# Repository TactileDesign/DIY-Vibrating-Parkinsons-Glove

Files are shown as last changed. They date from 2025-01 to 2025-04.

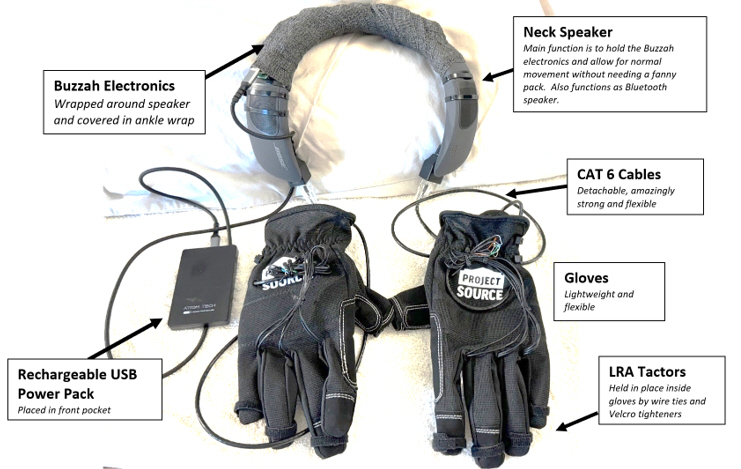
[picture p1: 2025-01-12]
1 - Buzzah Neck Build.jpg

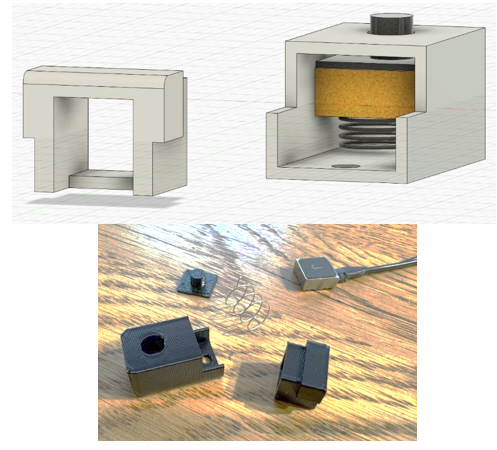
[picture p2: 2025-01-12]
1 - tactor.jpg

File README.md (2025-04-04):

# DIY Vibrotactile Parkinsons Glove (Neckbuild Buzzah Design)

This design makes use of Kris Wilk's Buzzah electronics design to drive LRA based tactors.  There are two things new in this build that add to Kris's design: 

1.  The gloves feature a new spring-based LRA tactor design that provides more energetic and focused vibrations than comparable foam-based LRA tactors.   When foam is used to decouple LRA tactors, significant energy is lost due to internal friction in the foam.  No energy is lost when using springs for this function since springs are almost perfectly elastic.  See the separate pdf for a detailed discussion of these new spring tactors.

2.  The electronics are housed on a bluetooth neck speaker.  This keeps the wires out of the way compared to fanny pack versions.  The bluetooth speaker can also sync with your smartphone as a speakerphone and mp3 player.

Note:  There are two files here.  The 'building description" file details how to build the gloves and tactor.  The "design considerations" file discusses theoretical issues regarding LRA-type tactors.

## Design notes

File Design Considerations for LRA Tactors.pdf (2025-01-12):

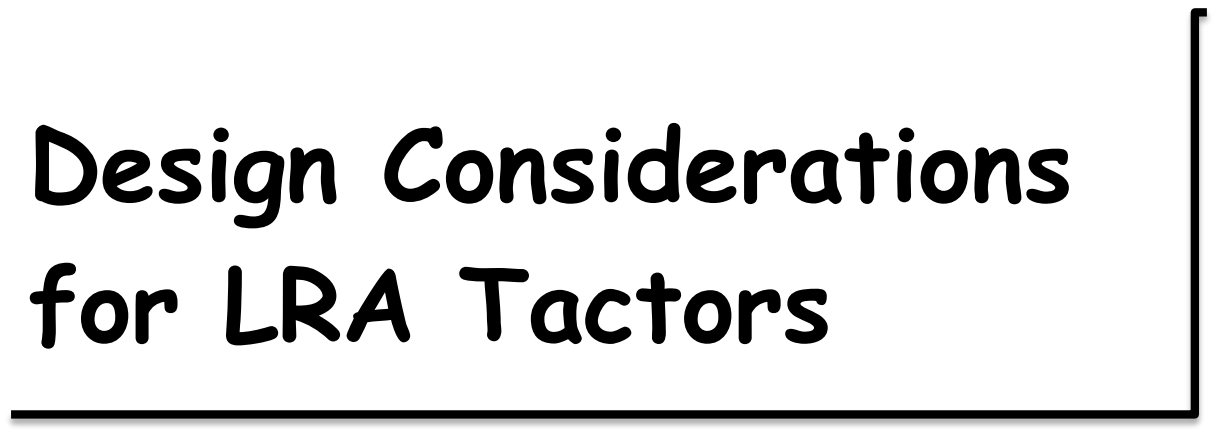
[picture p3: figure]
Design Considerations for LRA Tactors

### Introduction

What follows is a description of the theoretical design criteria that were considered in designing a tactor housing for a square shaped z-direction LRA. Detailed instructions and 3D print files for constructing tactors and fitting them to a glove are provided with the Buzzah neck build instructions. While I developed this tactor housing to use in my Buzzah Neck Build, but it would work in any LRA-based design.

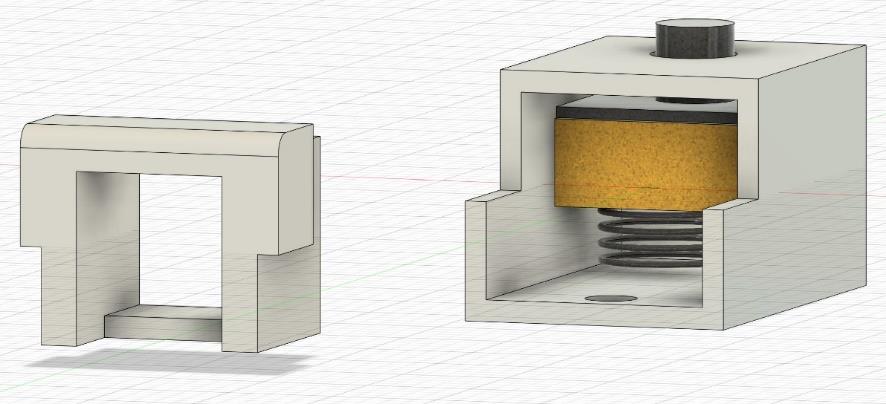
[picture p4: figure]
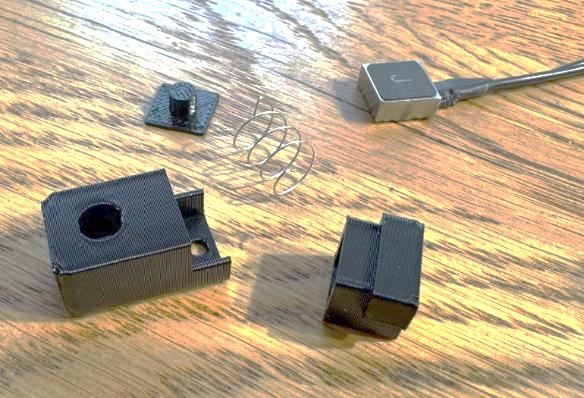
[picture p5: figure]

# Physical Principles of LRA Tactors

Imagine a paint can that is vibrates inside a shaker case as shown here. When the case pushes up on the can, Newton’s 3rd law tells us that the case must experience a downward reaction force
from the paint can. This downward force on the case does not create any motion of the
case because the case is “grounded” on a table which does not allow motion in the
downward direction. However, when the case alternatively pushes downward on the paint can, the inertia of the can results in an upward force on the case. If this upward force from the can is greater than the weight of the case, the case will be lifted off the table. The scenario just described is exactly analogous to what is going on in an LRA vibrator that is being driven by a Buzzah driver. Instead of having a paint can, the LRA
has a relatively massive magnet that is vibrates up and down inside its case, resulting in
the vibrations of the case we observe externally.

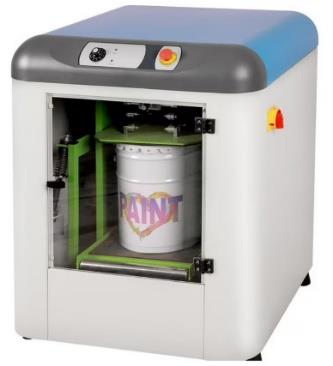
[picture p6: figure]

To illustrate the challenges of tactor design for an LRA, consider the following demonstration. In (A), a vibrating LRA vibrates vigorously off a table like the paint shaker our previous example. In (B), a finger pushes gently downward on the vibrating LRA. If you were to perform this experiment yourself, you would find that the LRAs vibration is quickly grounded out by the table, even with only a very slight pressure from your finger. However, if a weak spring is placed between the vibrating LRA and the tabletop as in (C), you would find that the LRA continues to vibrate vigorously up and down as long as you don’t push so hard as to completely compress the spring against the tabletop. As we design our tactor, we must likewise incorporate an elastic element within our tactor housing that allows a free up and down LRA vibration as in (C).

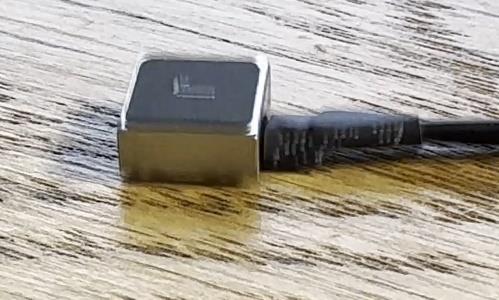
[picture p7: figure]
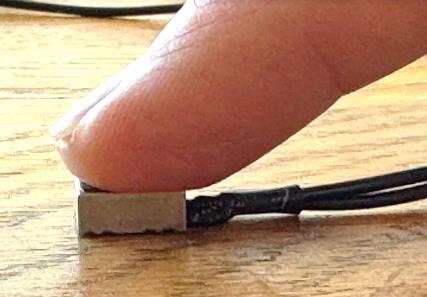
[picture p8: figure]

(A) | (B) | (C)

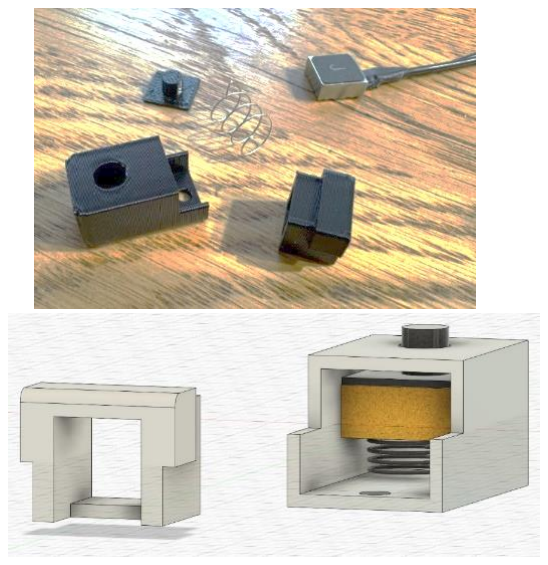
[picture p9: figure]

The 5 elements of the LRA tactor I designed are illustrated here. The LRA buzzer is sandwiched between a button plunger from above, and a weak spring from below. When the button is depressed, the internal plunger is pushed away from the top of the tactor housing. This keeps the LRA from mechanically grounding out to the top of the case which is itself grounded by the glove finger elastically holding the case against the fingertip. The LRA vibrates freely within its rectangular enclosure that is closed in by the endcap which is held in place by a tight friction fit. No fasteners are required. The endcap fits tight enough not to loosen from normal use, but not so tight that it cannot be removed with needle nose pliers. The window in the endcap is big enough to allow the electrical leads to exit, but small enough to keep the LRA and spring from vibrating out of their box inside the case. The hole in the bottom of the case allows the tactor to be attached inside a glove using a small plastic wire tie.

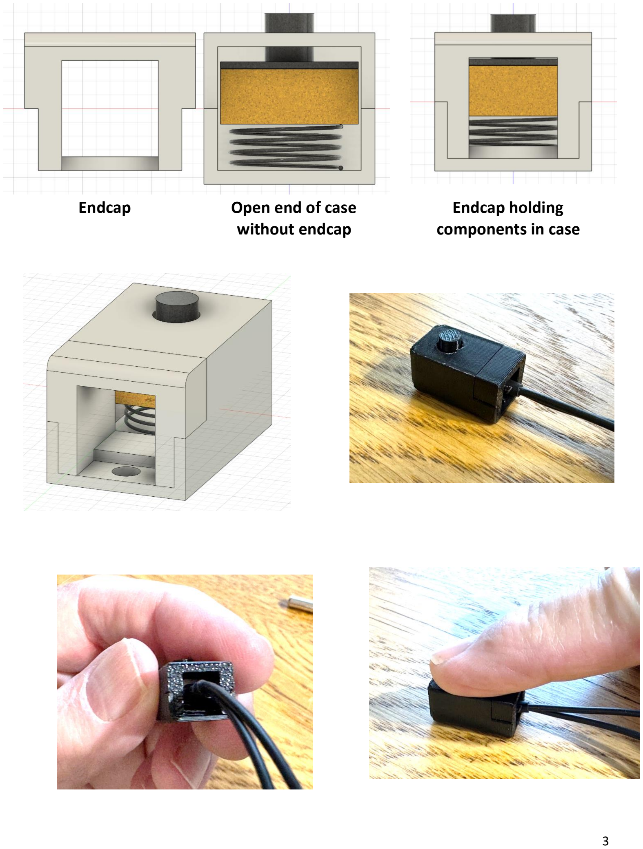
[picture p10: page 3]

Endcap | Open end of case | Endcap holding
| without endcap | components in case

# Determining Spring Characteristics

Before deciding to employ a spring to decouple the LRA from the tactor enclosure, I tried various types of springy foam and sponges collected from around the house and from various hardware store products. But all samples damped the vibration of the LRA to unacceptable levels. One can easily observe the damping effect that is introduced by foam by performing this simple test: In figure (A), a buzzer is hooked to an LRA driver and decoupled from the tabletop using a weak spring of length 11 mm. The buzz that is experienced with the spring is then compared to the same buzzer decoupled from the tabletop by foam with 11 mm thickness as we see in figure (B).

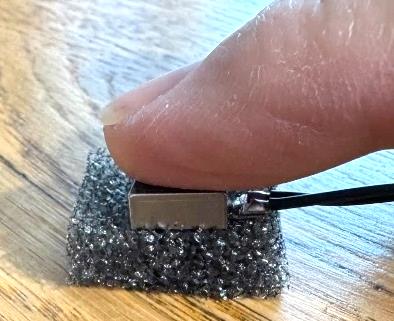
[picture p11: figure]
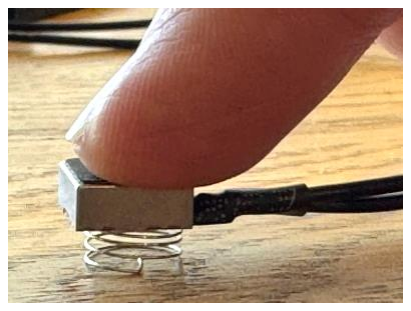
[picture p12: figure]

(A) (B)

When I performed this test, I found that the foam significantly damped the motion of the LRA buzzer compared to the spring. With the spring, the perceived buzz amplitude felt uniform, with no change in amplitude as I increased loading force as per Tass specifications to achieve the required 0.5 mm preload skin indentation. However, the foam gave a highly non-linear response, with perhaps 20% damping compared to the spring for very light preloading, and well over 50% damping for stronger preloading. There are two properties of the foam that caused this. First, all the foam I could find was too stiff, creating too strong coupling with the table, thereby grounding out vibrations. The stiffness of the foam appeared to increase non-linearly with increased deflection, leading to an observed rapid increase in damping at higher preloading. One might think we could solve the grounding problem if we could just find weaker foam. However, foam has another problem: It is inherently inelastic. Imagine trying to bounce a ball on foam and you realize the ball barely bounces because of the foam is eating up energy internally through damping. So, even if we could find a foam that feels sufficiently cushy, it would still be problematic due to its inherent damping characteristics.

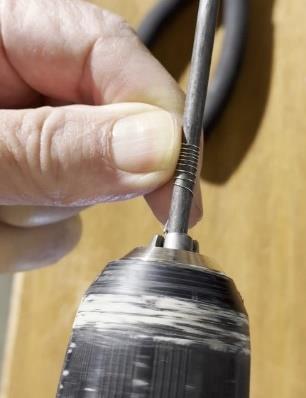
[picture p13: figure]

Finding a sufficiently weak spring with the proper dimensions as shown in figure (A) was a
challenge. There are plenty of springs on Amazon that are the right size, but they were all
way too strong for this application, creating too strong coupling between the tactor housing and LRA. Suppliers online such as https://www.thespringstore.com/ advertise 70 trillion springs available. However, 99.9999% of their springs are only available by special order, outrageously priced at $4-$10 per spring. Still in my design phase, I was still not sure about the ideal spring force constant, wire diameter, coil diameter, number of turns, and coil pitch, so special ordering high priced springs for testing was not a viable option. Then my wife suggested I make my own springs. It turns out they are very easy to make as illustrated here on YouTube: https://www.youtube.com/shorts/M9Lnm1P6_70 . After experimenting with the many parameters by trial and error, I finally settled on the criteria discussed below.

### Wire type

Once I had the idea to make my own springs, I quickly found that guitar strings were ideal for this purpose because they are cheap and come in many gauges. Looped end guitar string of diameter 0.012 inch proved to be idea. Each string makes up to 7 springs, but I would suggest buying 10 strings so you have plenty to for practice – total cost $11.90 on Amazon.

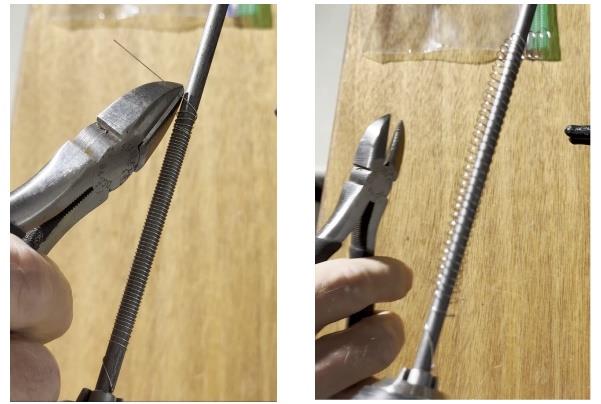
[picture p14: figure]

### Rod Diameter

The coil expands quite a bit after unwinding from the rod. And different gauge wire expands to make different diameter coils. Through trial and error, I found that 0.012-gauge wire yields a perfect spring diameter of 8.5 mm when wound and released from a 3/16” steel rod. An 8.5 mm diameter coil fits nicely under the 10 mm square LRA, and it is big enough that it does not vibrate out the wire window in the tactor. The rod can be purchased from Home Depot for $3.92 (see tools list). Note that the rod comes coated with very dirty oil and you will need to wash it and cut it down to about 18 inches before you start making springs.

### Number of Coils

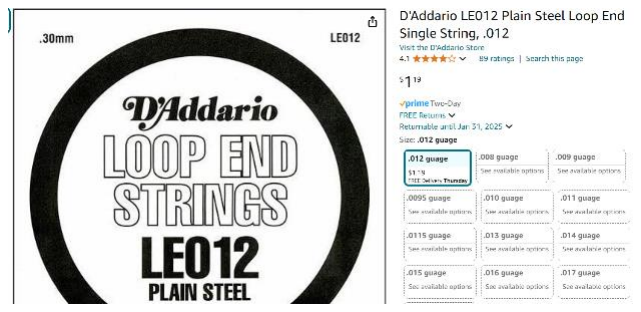
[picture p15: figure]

There are two factors to consider in determining the optimal number of coils to use in springs. We don’t want to have too many coils because, when the button is fully depressed, the compressed coils start taking up too much space in the bottom of the enclosure and can bottom out. Alternatively, having too few coils leads to too large of an angle between the spring and the LRA bottom which can cause binding in the chamber. After much experimenting, I ended up settling on the optimal number of coils to be 4.5. Having the half-coil on the end helps keep the spring from canting during use. As you see in the pictures shown below, I also put a small bend on either end of the spring to keep the ends from snagging and slipping up the side of the LRA.

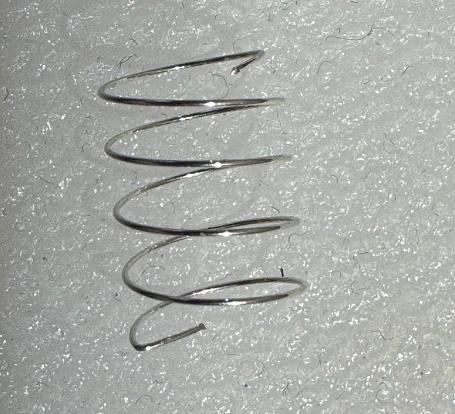
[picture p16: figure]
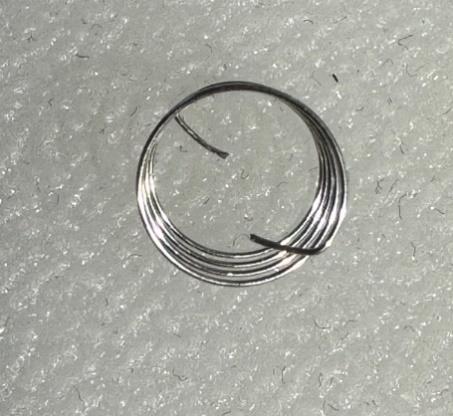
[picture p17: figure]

### Skin Preloading Displacement and Spring Rest Length

The crucial parameter of skin preloading displacement is perhaps the most important adjustable parameter of the tactor since it relates most directly to the quality of the vibration sensation that the tactor imparts to the fingertip. I accordingly spent a lot of time making sure I matched Dr. Tass’s specifications for this parameter as closely as possible.

In the diagram shown at right, we see the ideal 250 Hz tactor vibration signal that is to be applied to a fingertip in the Tass specifications from his device specs paper: https://pmc.ncbi.nlm.nih.gov/articles/PMC5624565/ . The vibration signal consists of a small 0.03 mm amplitude vibration from the buzzer on top of a 0.5 mm preloading displacement. The preloading
displacement is the distance the button contact protrudes into the skin when
the tactor is mounted to a fingertip before the buzzer vibration is applied.

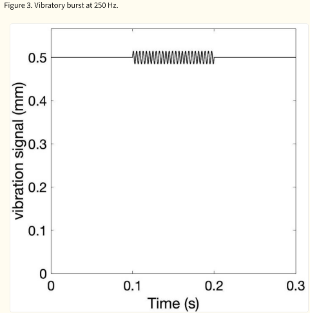
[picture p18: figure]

Consider the diagrams shown below to understand how preload skin displacement is achieved by our tactor/finger system through a balance between spring stiffness and skin elasticity. In (fig A), we see the spring at my ideal initial rest length, RL = 11 mm, which is coincidentally the same height as the case, C. In (fig B), the 11 mm spring is compressed to fit within case 4.5 mm cavity height, I, that exists under the rectangular LRA before the button is depressed. In (fig C), the button is depressed by an unseen finger, further compressing the spring below to a length, F. The fraction of the button extending over the top of the enclosure, and thus protruding into the fingertip skin, is the ideal preload skin displacement, PL = 0.5 mm. Figure C then illustrates what the button should look like under the finger when a tactor is mounted to the finger.

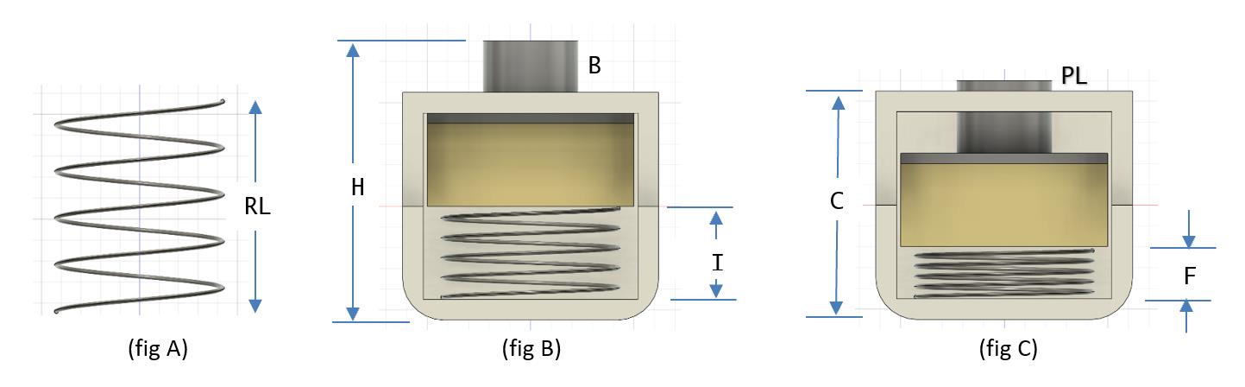
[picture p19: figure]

We see above that, since the button moves downward as the finger is positioned on the case, the preload skin displacement is not simply equal to the initial button height, B, above the case before the tactor is mounted to a fingertip. Instead, the preload skin displacement depends on the preloading force the spring exerts on the skin when the button is pushed. Since fingertip stiffness of the skin is much greater than that of the weak spring, most of the button travel is taken up by the spring, with only a fraction going into skin indentation.

The variable in our tactor that controls the magnitude of preload skin displacement for our tactor is the spring stiffness. As spring stiffness is increased, the preload skin displacement for a mounted tactor is correspondingly increased. The stiffness of a spring can be adjusted by small increments by changing its initial rest length. Stretching out a spring to have a longer initial rest length will make it stiffer. Winding a new spring with closer coils will result in a spring that is less stiff. If larger changes to stiffness are required, a new spring can be made with larger or smaller diameter guitar wire. Larger diameter wire leads to stiffer springs. We nominally use 0.012” diameter wire, but guitar wire comes in all diameter increments from 0.009” to 0.022”. However, only the gauges from 0.011” to 0.013” are likely to produce springs in a useful stiffness range for our tactor. As discussed previously, if you want to experiment with different gauge wire, you may need to use a different rod diameter to end up with a useable spring diameter.

Since spring tension can only be modified with the spring
outside the tactor housing, a process of trial-and-error testing
must be undertaken to determine the ideal spring rest length and wire diameter for a particular user.

There are three methods I devised to measure the preload skin displacement resulting from a particular spring in a mounted tactor. In method 1, I simply adjusted spring stiffness by trial and error to achieve a subjective perception of a relatively light preloading force that produced a robust and localized “zing” sensation on my fingertips when the spring was in a tactor
housing. Small changes in initial spring length result in
significant changes in spring stiffness. If a spring is stretched to

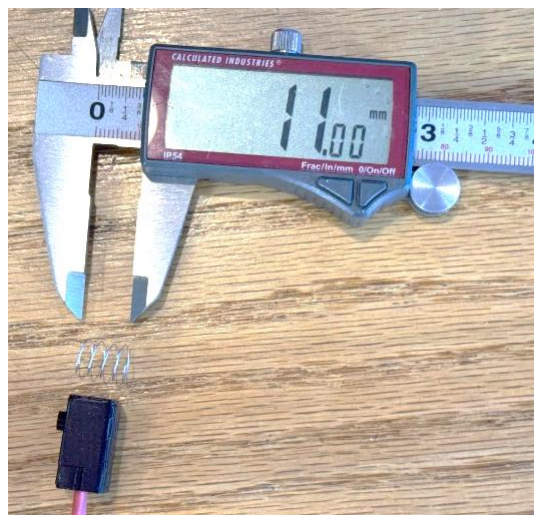
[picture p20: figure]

a longer initial length, the the preload displacement becomes greater, and the vibratory sensation increases. However, if a spring is too stiff, the vibrations cause finger bones to also vibrate which compromises therapeutic efficacy as Dr. Tass explains. If your spring is too strong, you need to make a new spring with closer coils and thereby less initial length. However, if a spring is too weak, therapeutic efficacy may also be compromised if the “zing” becomes too mild to clearly sense. I therefore sought to maximize the zing without getting vibrations transferring into my bones. Using the above trial-and-error method, I arrived at my ideal spring parameters of RL = 11 mm, number of coils = 4.5, and wire diameter = 0.012 inches.

While I was satisfied with the buzz sensation I achieved with these settings, I worried that my subjective method might not be yielding the proper Tass preload displacement of 0.50 mm. I therefore devised method 2, illustrated below, as an objective way to directly measure preload displacement and validate my subjective technique in method 1. In method 2, a special test tactor is 3D printed which has a 4 mm hole in its bottom surface. This hole in the bottom allows a feeler gauge to probe to the bottom of an LRA framed inside the assembled tactor. Note that two people are needed to perform this measurement.

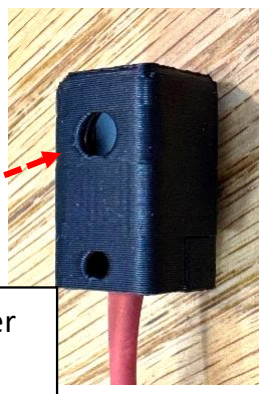
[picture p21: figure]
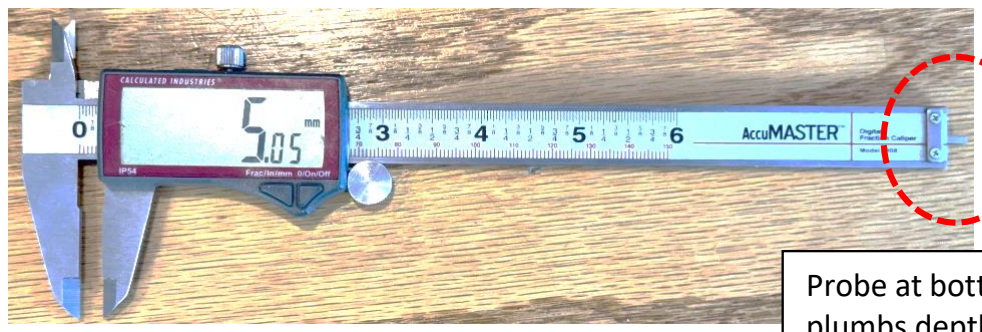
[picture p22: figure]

Probe at bottom of caliper plumbs depth of LRA
through hole in bottom

The difference in probe depth, before and after the tactor is mounted to a fingertip, yields the change in chamber height, I – F. The change in chamber height is likewise equal to the change in button height that occurs when the finger is mounted on the tactor.

Cℎange in Cℎamber Heigℎt = Cℎange in Button Heigℎt

I − F = B − PL

The tactor preload displacement, PL, is then found by,

PL = B − (I − F)

The initial button height, B, can be precisely found by subtracting the case height, C, from the initial overall tactor height, H,

Initial Button Heigℎt = Overall Tactor Heigℎt − Case Heigℎt

B = H − C

Plugging in the actual measurements I made on my test tactor using an 11 cm spring with 4.5 coils, I obtained,

PL = | H | − | C | − | (I | − | F)

= 13.4 mm − 10.94 mm − (5.01 mm − 3.03 mm) = 0.48 mm

Happily, method 2 verified that the ideal 11 mm spring rest length that I subjectively obtained from method 1, yielded a measured preload 0.48 mm skin displacement that was quite close to the ideal 0.50 mm value that is specified my Dr. Tass.

The above measurements were made under ideal conditions while sitting motionless at a desk. Under less ideal conditions, users may be picking things up or pushing on some external surface. When the tactor is squeezed between a fingertip and some external object, the finger will exert a stronger force against the spring and cause preload displacement to be reduced. When this happens, the perceived vibrational amplitude is increased by about 20%. I don’t view this necessarily as bad since Dr. Tass has suggested some modulation of amplitude might actually be helpful in therapy. Note also that the above measurements were taken on an early tactor prototype. After further testing I reduced the button shaft height by 0.3 mm to allow for a bit more room for the compressed spring to keep it from bottoming out when the button is depressed.

Note that my case measurements, H and C, used above do not exactly match the corresponding parameter settings I had programmed into my 3D printer. For example, I had my case height set at 11 mm in my printer, but it actually came out to be 10.94 mm when measured. Therefore, H and C had to be measured on a real tactor because of the slight deviations that occur in the process of printing.

While method 1 and method 2 both provide reliable ways to adjust spring stiffness for individual users, I worried that these methods may not be easy to replicate by novice tactor builders. I then devised a third method based on subjective protrusion feel that is much easier to implement for a novice. In method 3, a set of solid reference tactors are 3D printed with fixed PL button heights of 0.3 mm, 0.4 mm, 0.5 mm, 0.6 mm and 0.7 mm. The test tactors are used as tactile references for users to compare to the feel of a preload displacement being caused by a spring in a tactor that is being tested. The objective in method 3 is to determine an initial spring length that yields a strong localized “zing” when the button is depressed to a height equivalent to the 0.5 mm reference tactor. The additional references are provided to demonstrate to the user what “too high” or “too low” feels like.

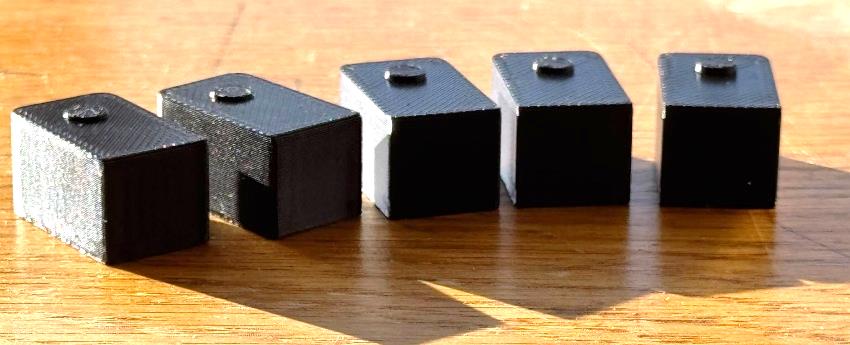
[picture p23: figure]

Dummy tactors used to demonstrate the feeling of the ideal preload displacement

### Tactor/Finger Mounting

When the tactor is mounted to a fingertip, its entire top surface should be making contact with skin to help block skin vibrations from the button from moving beyond the button area as per Tass specifications. The process of determining the proper tightness by which the tactors are lashed to the fingertip must be performed in concert with the above process to determining spring stiffness. If a tactor is lashed too tight, it will depress the button too far when using a particular spring and result in vibrations that vibrate into finger bones. If you lash the tactor too loosely, the button will be less depressed and result in weaker vibrations. The tactor needs to be tight enough not to slip off the finger during normal use, but not so tight as to cause discomfort. The reference tactors from method 3 above can also be used to help gauge the tightness that achieves proper PL height. Velcro fingertip tighteners are the most reliable way to achieve a precise and reliable lashing that does not stretch out over time. However, I find the Velcro tighteners too annoying because of the loss of dexterity and the fact they tend to grab to fabrics I touch. I alternatively spent much time and energy to find a glove that has the proper finger diameter and elasticity to hold the tactors to my fingers with the correct preloading force. In my quest to find the perfect glove that could be used without Velcro, I tested nearly 20 pairs of gloves from Lowes and Home Depot. I describe my glove choice later in the building section of this grand treatise.

### Initial Button Height

The current tactor I use is designed to have a nominal button height, B = 2.2 mm. The chamber that houses the spring and LRA ostensively allows for I = 4.5 mm of button travel since the LRA thickness is 4.0 mm, the case thickness is 1.0 mm, and the flange thickness is 0.5 mm. Using a button shaft height of 3.2 mm yields F = 2.8 mm in the bottom of the chamber to accommodate the compressed spring windings. The 2.8 mm also allows sufficient space to accommodate the 0.03 mm vibration amplitude along with occasional over-compression which occurs when
picking up heavy objects, and
possible variances occurring in the 3D printing process.

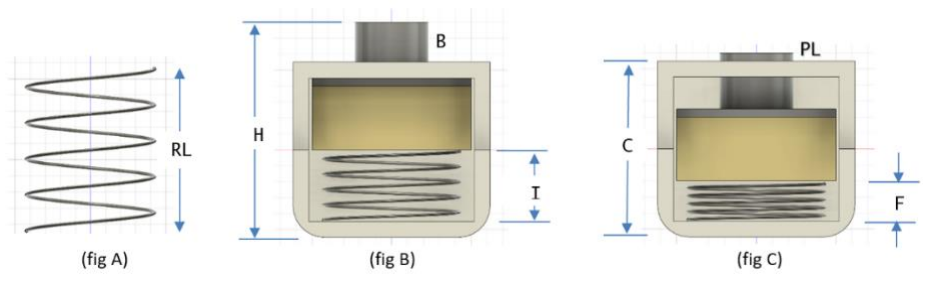
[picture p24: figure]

One might think that the nominal 9 mm chamber height could be reduced if B was reduced in order to make a smaller tactor. However, there is a practical concern that requires B to be at least 1 mm. Before the button is depressed, the button flange is forced up against the inside chamber ceiling by the spring. This flange must be pushed clear of inner ceiling of the finger mount in order to facilitate the free vibration of the LRA. Since the vibrational amplitude is only 0.03 mm, the clearance of the button flange from the inner chamber ceiling might not seem to be an issue. However, the top of the spring is angled slightly due to coil pitch, so there is a tendency for the button flange to be slightly canted by the top of the spring. In practice, I found that the flange needs to be pushed in at about 1 mm to safely clear the inside enclosure ceiling and allow free LRA vibration. So, theoretically, B could have been reduced in the tactor design (requiring a slightly stiffer spring). With B = 1.0 mm, the user would only need to depress the button by 0.5 mm to achieve the proper PL. However, when I tested tactor designs with shorter B heights, I found it was too easy for the button to slide off my fingertip when I was performing activities with my hands. With B = 2.2 mm, the buttons reliably remain in contact with my fingers, actively providing therapy, when performing activities that jostle the tactors.

### Vibrational Amplitude

The vibrational amplitude of the LRAs in this tactor design is set in the Buzzah software. In all the measurements described previously, I had my amplitude set at 100%. Unfortunately, I could not think of any simple way to actual measure the vibrational amplitude to verify that it matched the 0.03 mm amplitude in the Tass specifications. So, this is a parameter that we must adjust based on user perception. My philosophy when adjusting amplitude is to deliver the highest vibrational amplitude that does not feel like it vibrates into my finger bones. The 100% Buzzah setting yields a stronger perceived fingertip vibration when using the tactor compared to how I used to apply my treatment with an LRA held directly to my fingertip without a tactor. Even though the buzz is stronger when using this tactor, I have left the amplitude at 100% since it does not feel like it is going into my bones when spring tension and mount tightness are adjusted as described above. If I ever felt like I was getting too much vibrational amplitude, I could adjust it lower in the software settings. However, I could not obtain a larger amplitude since I am already at the high limit of my dynamic range without increasing PL.

In summary, skin preload displacement and amplitude are adjusted by trial and error to achieve sufficient zing to clearly sense, but not too much zing as to vibrate areas other than the fingertip. Since there is a variability in the elasticity of different user’s skin elasticity, be aware that the setting that works best for my tactors may not work best for you. Velcro tighteners on fingertips help to achieve uninterrupted therapy while doing things, but also result in less dexterity. The table below illustrates measures that can be taken to increase or decrease skin preload displacement and amplitude if you feel your tactor zing needs adjustment.

Preload Adjustment | Action Taken
To increase preload displacement and increase zing sensation | 1. Slightly stretch spring out to increase initial length 2. Make a new spring with using larger diameter wire (Note: You may also need to change your rod diameter to end up with proper coil diameter if you change wire diameter)
To decrease preload displacement and decrease zing sensation | 1. Make a new spring with closer coils 2. Make a new button with a shorter shaft 3. Make new spring with using 0.011 diameter wire
To adjust buzz amplitude independent of preload displacement | 1. Adjust amplitude in Buzzah software settings

### Button Diameter

The diameter of the button contact area is not specified by Dr. Tass, however, his tactor manufacturer indicates the 2021 tactors have a contact diameter of 5.1 mm. (See, https://images.hu-production.be/response/460df2ac-7e99-4988-ad8c-cfe50970ad2a.jpg (https://images.hu-production.be/response/460df2ac-7e99-4988-ad8c-cfe50970ad2a.jpg) ) We tested button diameters of 5.1 mm, 4.6 mm, 3.6 mm, and 2.6 mm with the idea that smaller diameter might give a more point-like
vibrational sensation. But smaller diameter buttons also resulted in less
perception of the vibrational zing amplitude. So, we quickly eliminated 2.6 mm

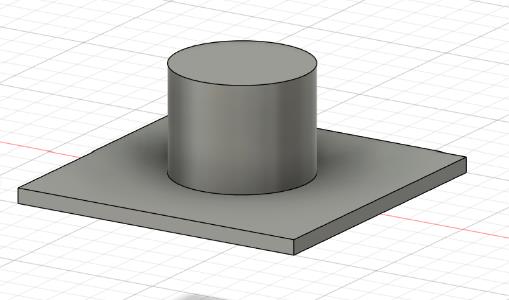
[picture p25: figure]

from consideration. Since button diameters of 5.1 mm, 4.6 mm and 3.6 mm all gave almost identical vibrational sensations, we settled on 5.1 mm used by engineering Acoustics in the link above. The hole we use in the top of the tactor enclosure is currently 5.5 mm to allow free movement of the button shaft, however, we are currently exploring feasibility to increase the size of the enclosure hole to provide a somewhat larger undamped skin area as is found in the Engineering Acoustics tactor.

### Friction Between Button Plunger and Inside of Case

The rectangular button flange has edge length of 10 mm which is the same size as the
LRA. The inner rectangular chamber is 10.4 mm in length and width, allowing for a 0.2 mm tolerance around all edges to facilitate up/down movement. As the button flange and LRA vibrate, they rub slightly against the walls and create a small amount of friction. Given that the button vibration remains vigorous in spite of this friction, we may ignore any damping effects caused by the friction. The rubbing also produces
some vibration of the case during treatment, however, the vibration sensation from
button on the fingertip is much greater than that of the case. So, even though the case

is vibrating somewhat during treatment from the rubbing on walls, this vibration is very small compared to the button and does not significantly detract from the localized point-like vibration sensation that is required in the Tass vCR treatment. The user can easily gauge the effect of the case vibration during treatment by grounding the tactor to a tabletop during use. When this is done, the case vibration is eliminated and the perceived intensity of the vibration goes up by approximately 20%. The 2021 Tass tactors inherently have less case vibration because the acoustic exciters are so massive. If one wanted to minimize case vibration of this LRA tactor, the mass of the tactor case could be increased by making thicker walls, or somehow affixing small lead weights to the tactors.

Finally, another effect from the rubbing is that the LRA tactors are 2-3 times audibly louder than simply having the LRAs mounted in gloves without a tactor. While the sound is not “loud” by any standard, it is noticeably “louder” than the LRA without a tactor. Perhaps the tactor might be quieter if the walls were made thicker.

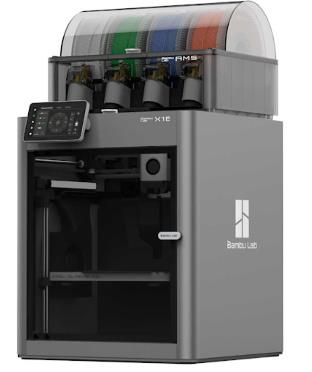
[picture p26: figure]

### 3D Printing Filament Type

In all of my early testing, I used PLA to print the print parts. When using PLA, the button hole came out very circular. I switched to ABS for final printing once I had my design criteria settled because I wanted to go with the strongest material. I then noticed that the button hole in the top was coming out with a more oval shape. This does not seem to have had any negative effect on the motion of the button. However, the fit of the endcap became too loose when switching to ABS and I had to reduce my tolerance to zero to get an ideal tight fit. I think PLA is probably strong enough to use for a tactor print. However, be aware if you use PLA to print, you might need to adjust your endcap tolerance so your fit will not be too tight. Also, different printers have varying print characteristics and may require slight adjustments to endcap tolerance.

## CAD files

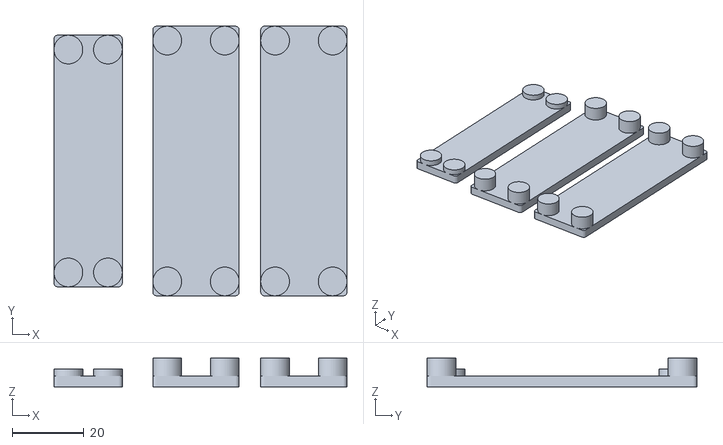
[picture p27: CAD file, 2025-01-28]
3D Boards Homespot v4.stl
81.5 x 75.0 x 8.00

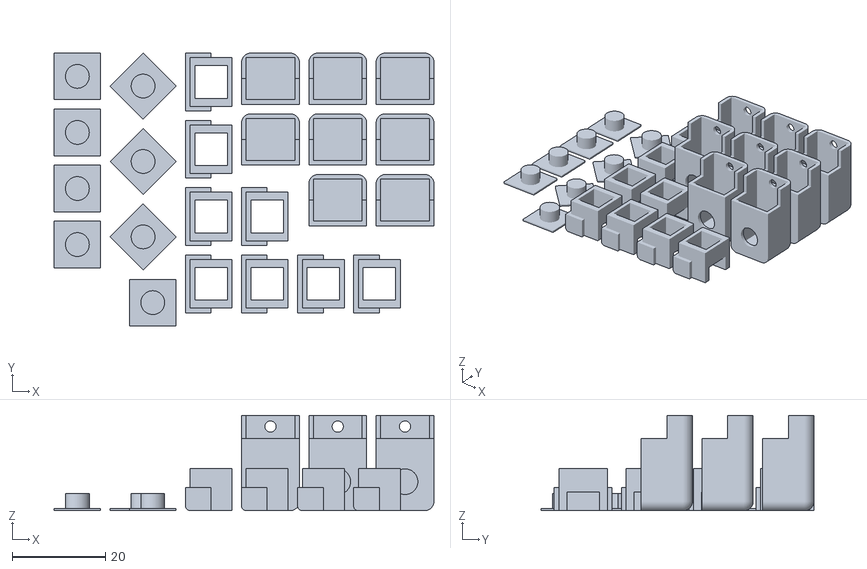
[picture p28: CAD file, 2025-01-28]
3D 8 Tactors 1208 5-1 mm Update (v4).stl
81.3 x 58.4 x 20.4
